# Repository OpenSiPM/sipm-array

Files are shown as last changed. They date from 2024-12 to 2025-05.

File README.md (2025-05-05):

# sipm-array
Schematics and layouts for SiPM arrays

# tia-s14160-x4
This contains schematics and PCB layouts for a 4 channel SiPM detection board used for parallel laser scanning.  Each channel implements the standard OpenSiPM transimpedance amplifier, pole zero cancelation, and low pass filtering to produce a Gaussian single photon response.  



# impulse response
X4-33nh-3 0-30-lpf-470nh-100pf (channel3)

# power supply
The X4 design uses the standard OpenSiPM power supply and bias generator boards.  Due to the higher current from running 4 SiPMs in parallel, the LT8362 bias generator is recommended for maximum dynamic range, although both designs will work.  Additionally the board can be configured to use two separate power supplies by ommitting resistors and plugging in two supply boards to both sockets.  However, in normal useage this is not required and is probably not useful as the current demand is low enough that a single supply is adquate.

# Non-descanned detection arm
Zemax simulation for non-descanned detection using the 4 channel SiPM board and the prescription for the lens array used can be found [here](https://github.com/OpenSiPM/sipm-array/tree/main/Zemax). 

# publication
A manuscript is forthcoming.

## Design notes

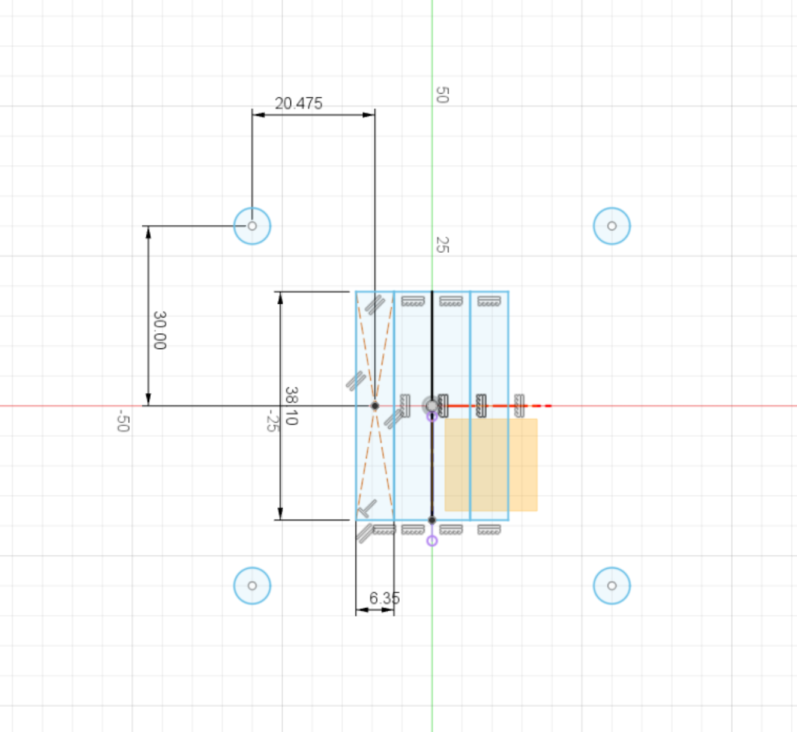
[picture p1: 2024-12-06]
mechanical diagram.png

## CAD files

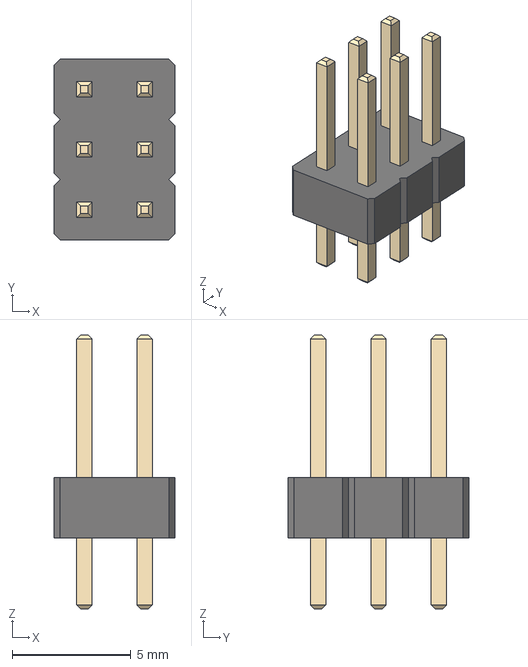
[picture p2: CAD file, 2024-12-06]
step/PinHeader_2x03_P2.54mm_Vertical.step
5.08 x 7.62 x 11.5 mm

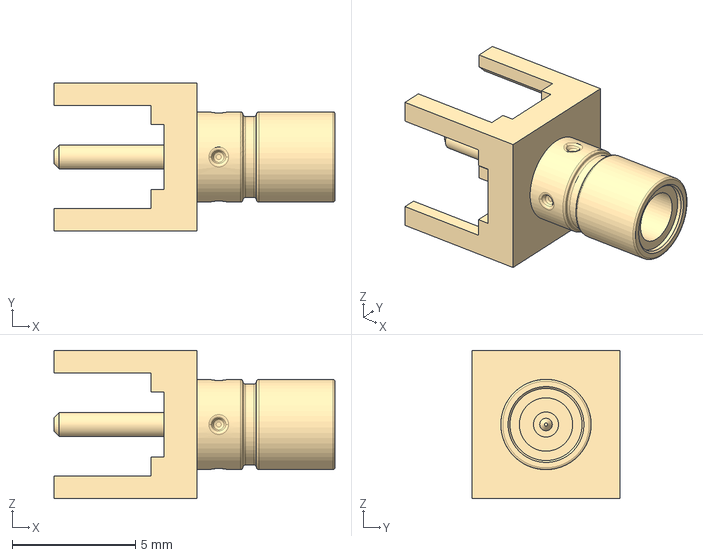
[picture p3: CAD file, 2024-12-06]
step/131-3701-261.stp
11.4 x 5.99 x 5.99 mm

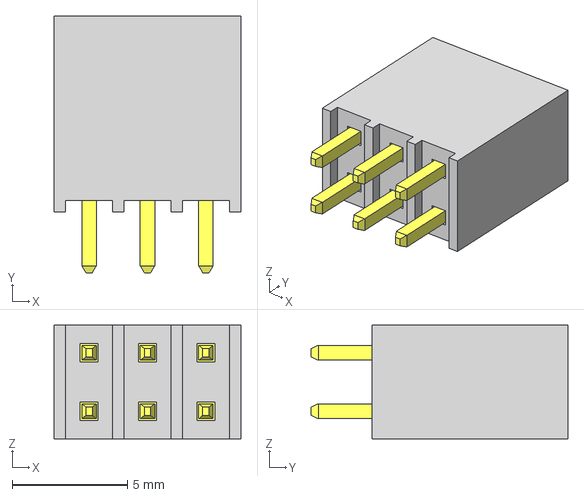
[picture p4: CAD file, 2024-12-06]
step/SSQ-103-01-G-D.step
8.13 x 11.2 x 4.95 mm
_T1SSQ-103-01-G-D
_P2SSQ-103-01-G-D

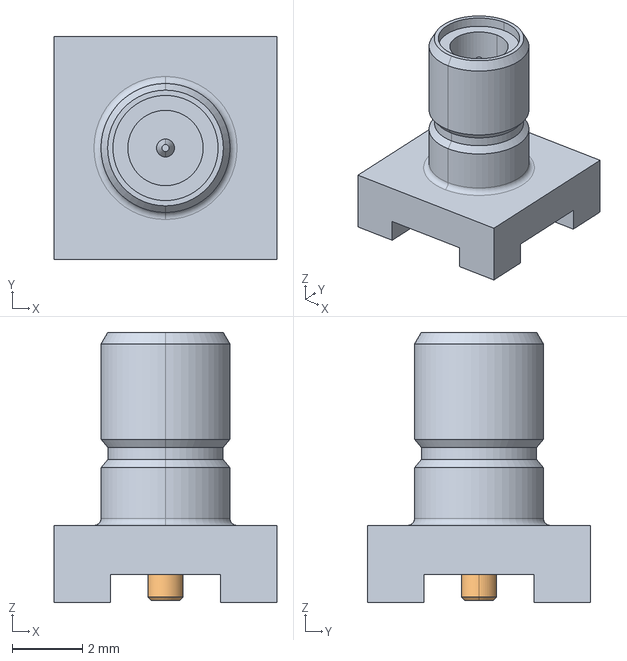
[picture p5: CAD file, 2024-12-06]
step/c-1-1337604-0-d-3d.stp
6.35 x 6.35 x 7.70 mm

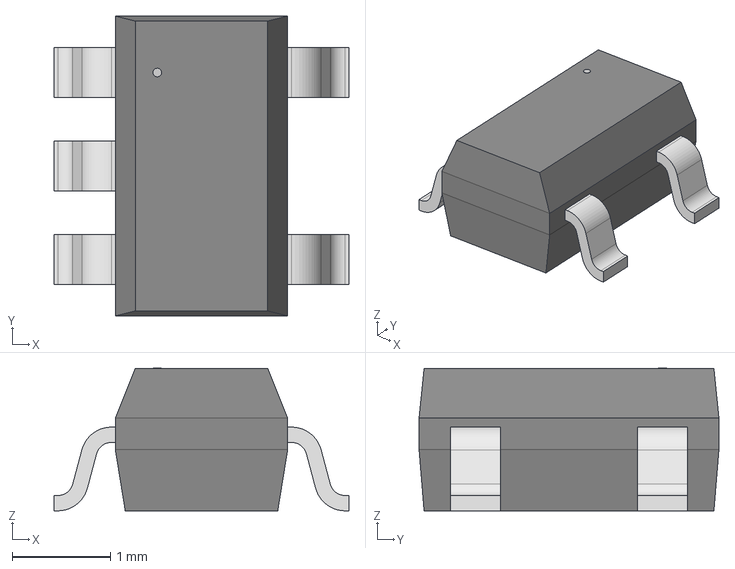
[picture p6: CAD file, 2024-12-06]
step/DBV5.step
3.00 x 3.05 x 1.45 mm

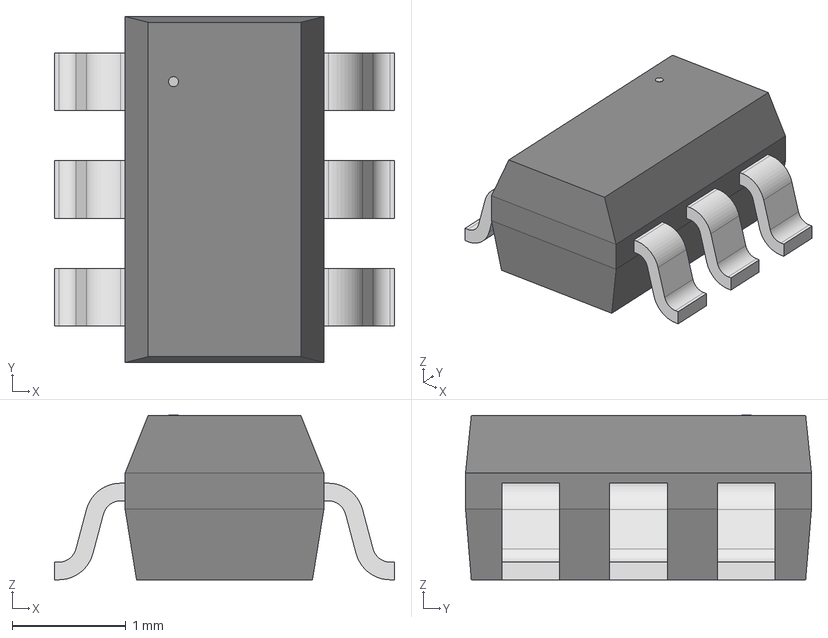
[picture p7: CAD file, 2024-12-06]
step/DBV6.step
3.00 x 3.05 x 1.45 mm

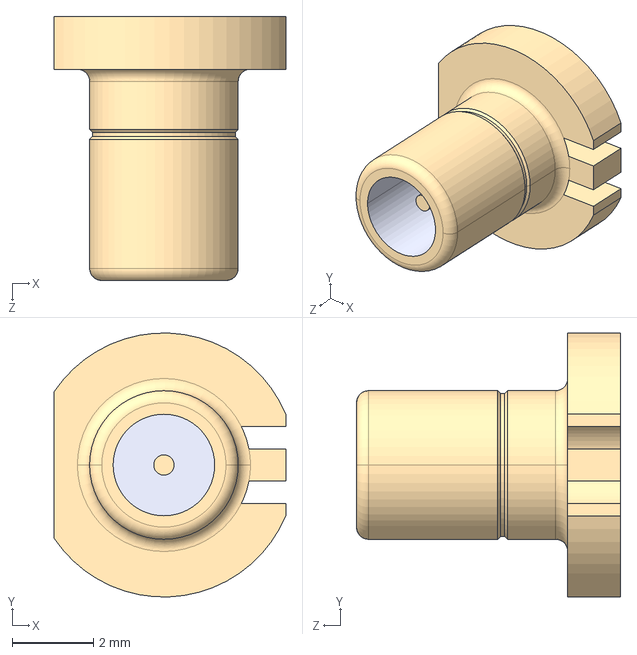
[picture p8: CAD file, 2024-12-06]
step/SMBR004D00.step
5.70 x 6.49 x 6.50 mm

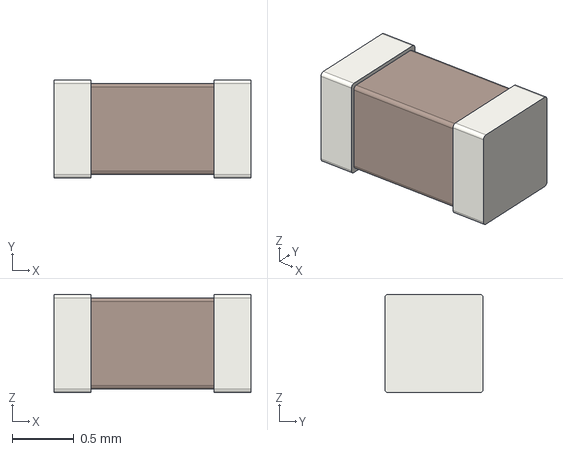
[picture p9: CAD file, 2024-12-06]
step/C_0603_1608Metric.step
1.60 x 0.8 x 0.8 mm

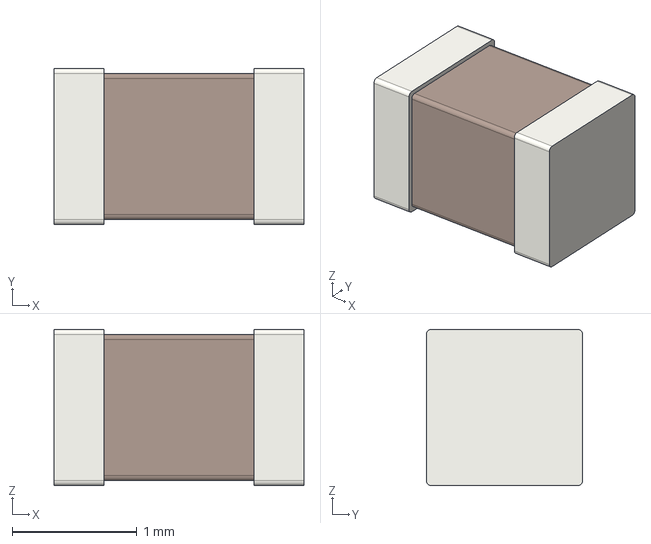
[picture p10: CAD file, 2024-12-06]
step/C_0805_2012Metric.step
2.00 x 1.25 x 1.25 mm

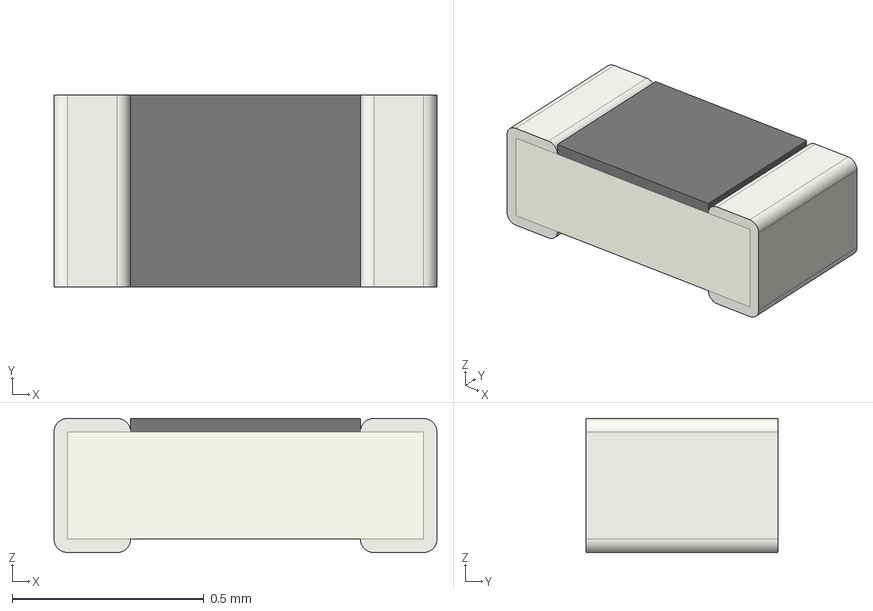
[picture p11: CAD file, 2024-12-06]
step/R_0402_1005Metric.step
1.00 x 0.5 x 0.35 mm

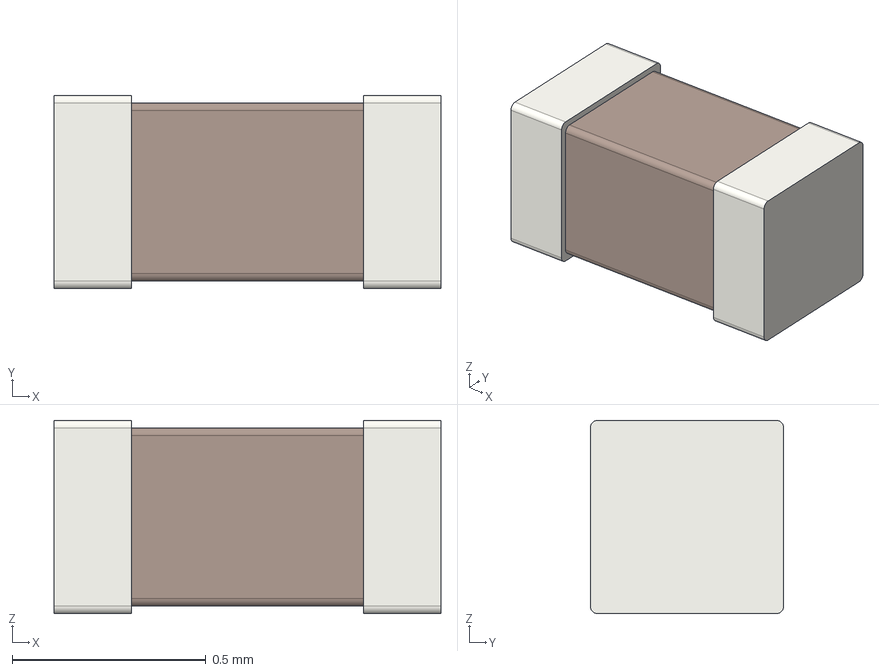
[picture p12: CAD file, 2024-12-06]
step/C_0402_1005Metric.step
1.00 x 0.5 x 0.5 mm

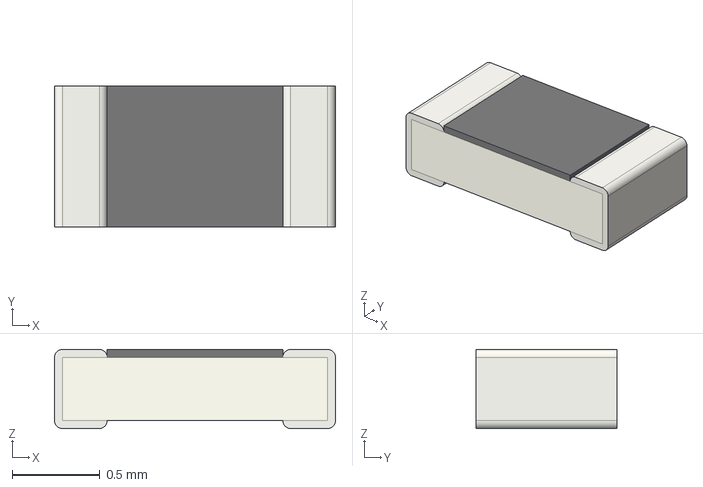
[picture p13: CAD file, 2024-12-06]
step/R_0603_1608Metric.step
1.60 x 0.8 x 0.45 mm

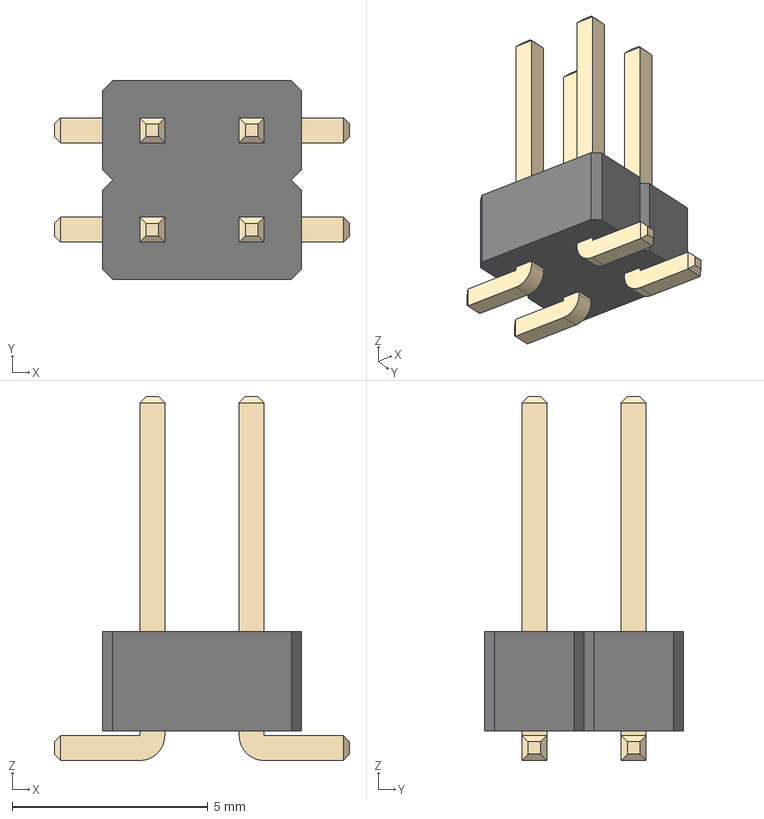
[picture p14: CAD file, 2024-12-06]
step/PinHeader_2x02_P2.54mm_Vertical_SMD.step
7.54 x 5.08 x 9.30 mm

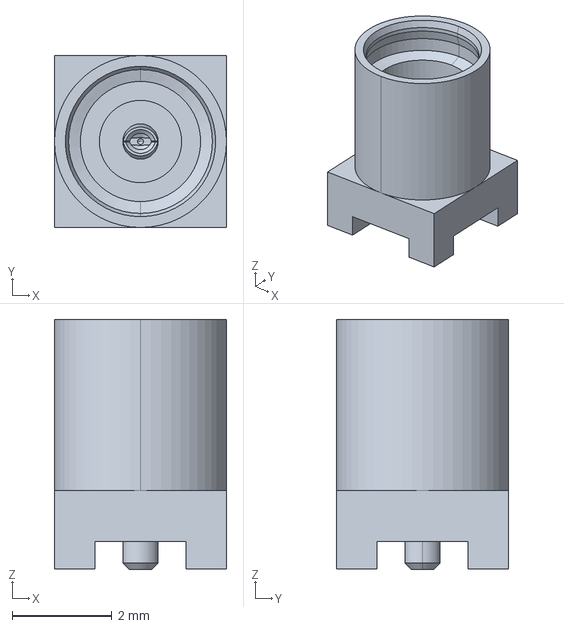
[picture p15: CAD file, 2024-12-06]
step/73415-2061.stp
3.45 x 3.45 x 5.01 mm

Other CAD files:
step/L_0603_1608Metric.step
step/S14160-3010PS_v3.step
step/S14160-3015PS v2.step
step/131-3701-261_old.stp
step/SMBR004D00.SLDPRT

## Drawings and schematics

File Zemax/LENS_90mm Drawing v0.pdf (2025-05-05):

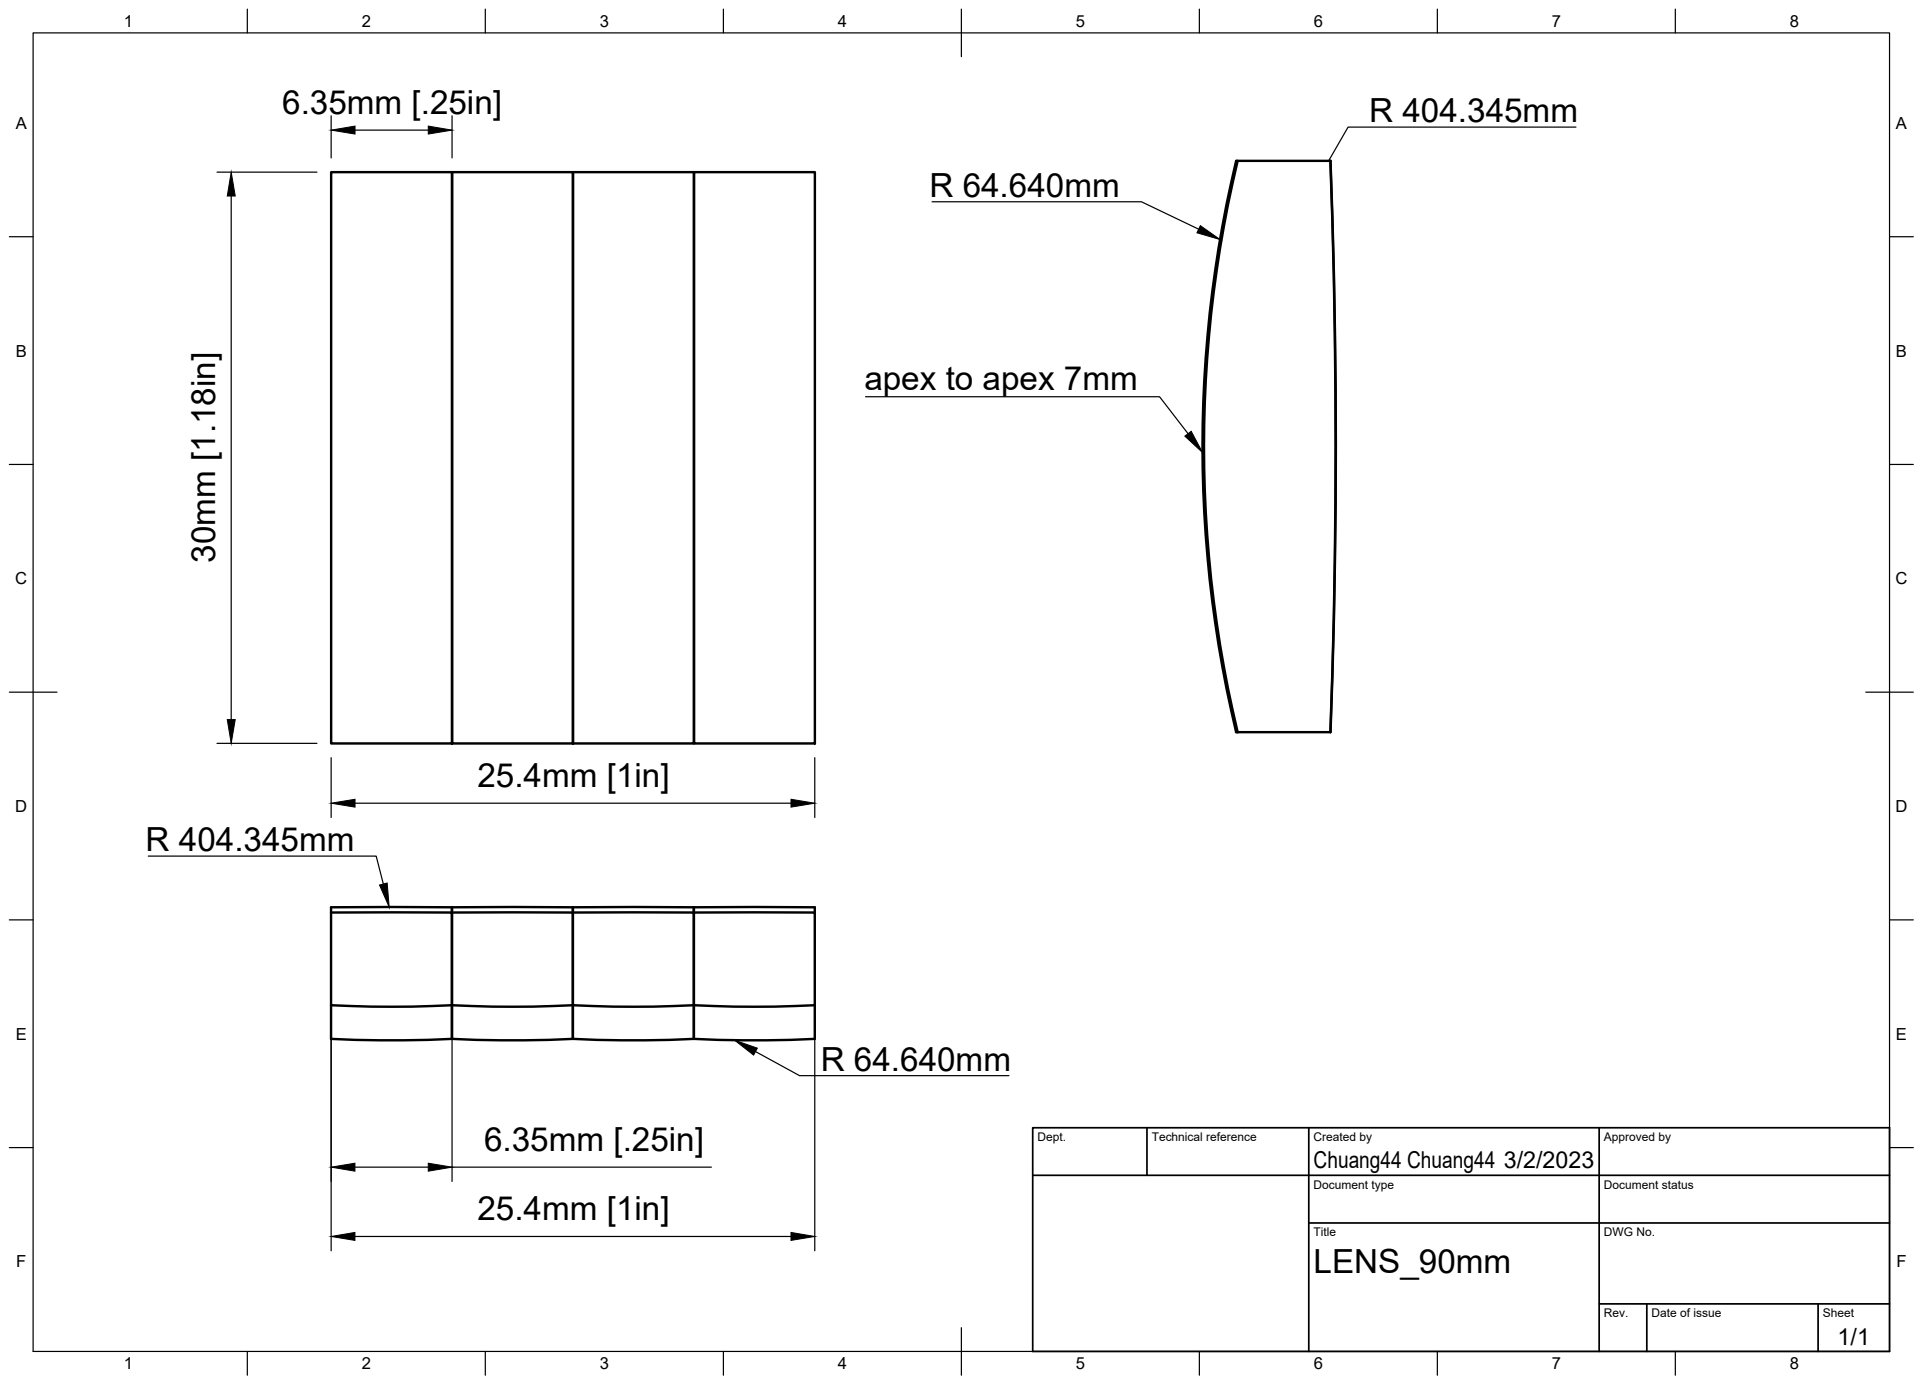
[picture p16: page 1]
Title; DWG No.; Rev.; Date of issue; Sheet; apex to apex 7mm

Dept. | Technical reference | Created by Chuang44 Chuang44 3/2/2023 | Approved by

Document type | Document status

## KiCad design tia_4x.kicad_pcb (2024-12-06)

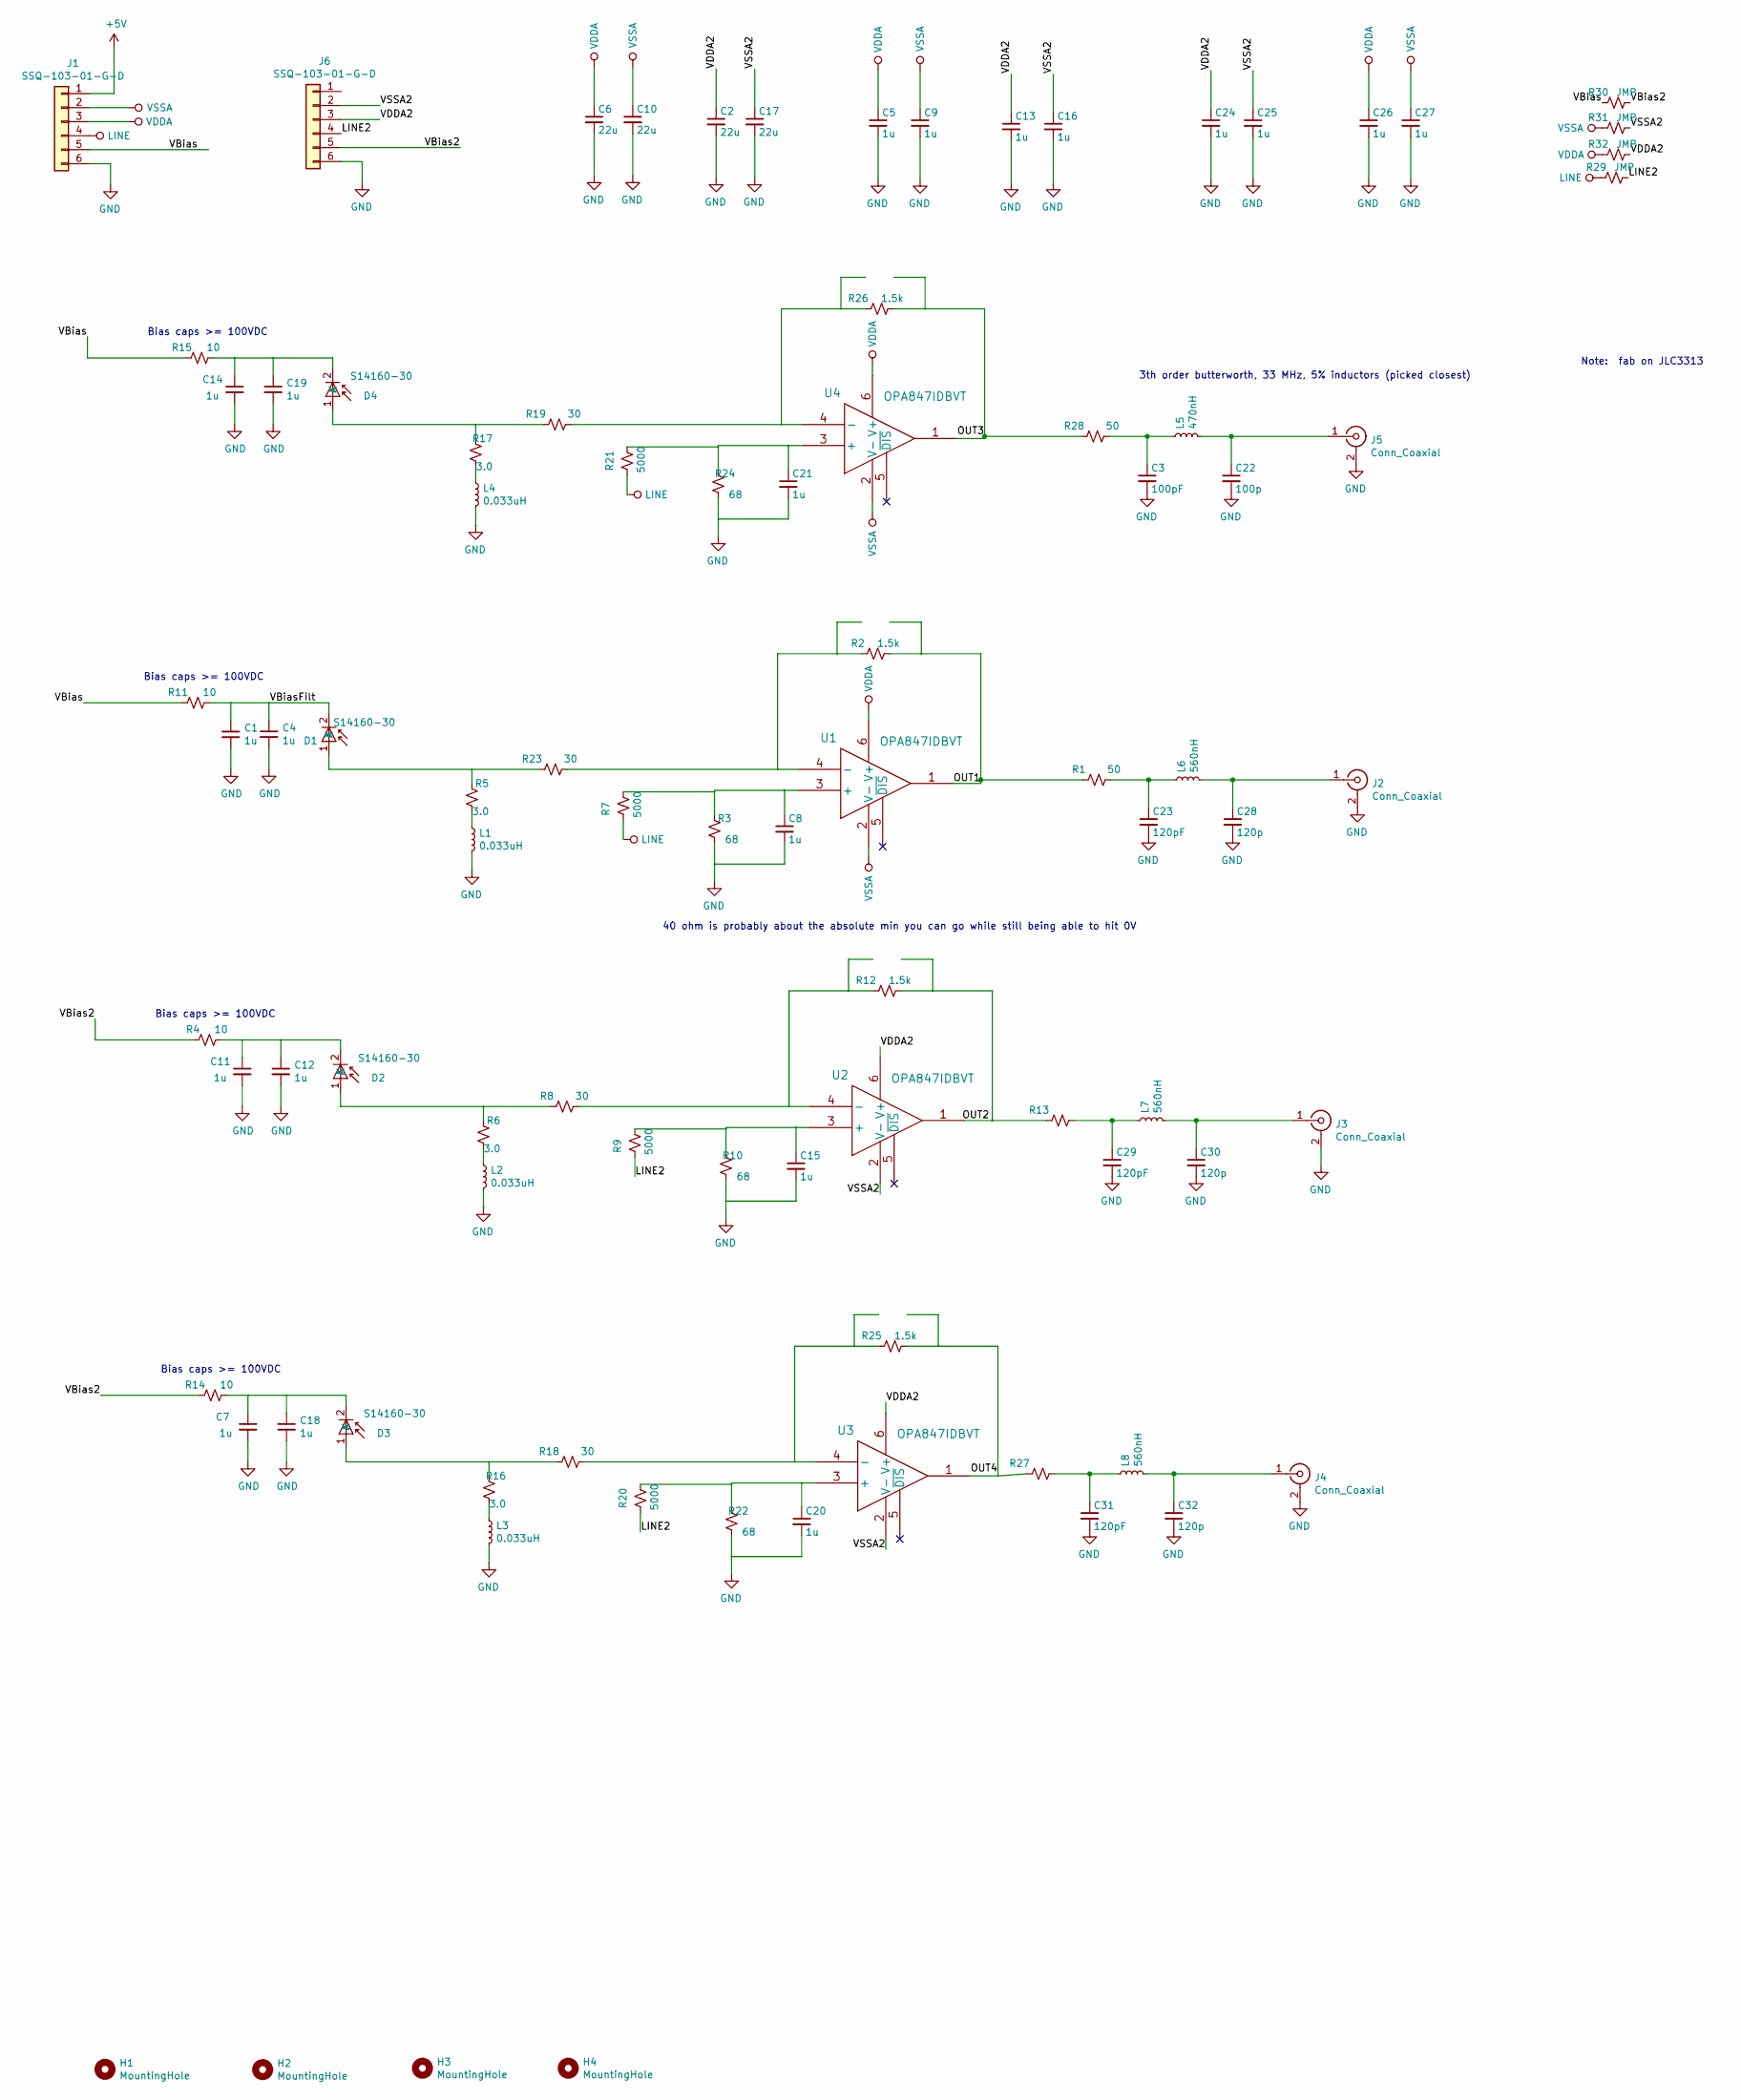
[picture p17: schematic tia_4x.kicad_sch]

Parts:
C1, C4, C7, C11, C12, C14, C18, C19: 1u; C_1206_3216Metric
C2, C6, C10, C17: 22u; C_0603_1608Metric
C3: 100pF; C_0402_1005Metric
C5, C8, C9, C13, C15, C16, C20, C21, C24, C25, C26, C27: 1u; C_0402_1005Metric
C22: 100p; C_0402_1005Metric
C23, C29, C31: 120pF; C_0402_1005Metric
C28, C30, C32: 120p; C_0402_1005Metric
D1, D2, D3, D4: S14160-30
H1, H2, H3, H4: MountingHole; MountingHole_6mm
J1, J6: SSQ-103-01-G-D; PinHeader_2x03_P2.54mm_Vertical
J2, J3, J4, J5: Conn_Coaxial; SMB_Jack_Vertical; Digikey WM5528-ND
L1, L2, L3, L4: 0.033uH; L_0603_1608Metric
L5: 470nH; L_0402_1005Metric; part MLF1005GR56JTD25
L6, L7, L8: 560nH; L_0402_1005Metric; part MLF1005GR56JTD25
R1, R13, R27, R28: 50; R_0402_1005Metric
R2, R12, R25, R26: 1.5k; R_0402_1005Metric
R3, R10, R22, R24: 68; R_0402_1005Metric
R4, R11, R14, R15: 10; R_0402_1005Metric
R5, R6, R16, R17: 3.0; R_0402_1005Metric
R7, R9, R20, R21: 5000; R_0402_1005Metric
R8, R18, R19, R23: 30; R_0402_1005Metric
R29, R30, R31, R32: JMP; R_0402_1005Metric
U1, U2, U3, U4: OPA847IDBVT

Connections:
+5V: J1.1
/LINE2: J6.4, R9.2, R20.2, R29.2
/OUT1: R1.1, R2.2, U1.1
/OUT2: R12.2, R13.1, U2.1
/OUT3: R26.2, R28.1, U4.1
/OUT4: R25.2, R27.1, U3.1
/VBias: J1.5, R11.1, R15.1, R30.1
/VBias2: J6.5, R4.1, R14.1, R30.2
/VBiasFilt: C1.1, C4.1, D1.2 (K), R11.2
/VDDA2: C2.1, C13.1, C24.1, J6.3, R32.2, U2.6 (V+), U3.6 (V+)
/VSSA2: C16.1, C17.1, C25.1, J6.2, R31.2, U2.2 (V-), U3.2 (V-)
GND: C1.2, C2.2, C3.2, C4.2, C5.2, C6.2, C7.2, C8.2, C9.2, C10.2, C11.2, C12.2, C13.2, C14.2, C15.2, C16.2, C17.2, C18.2, C19.2, C20.2, C21.2, C22.2, C23.2, C24.2, C25.2, C26.2, C27.2, C28.2, C29.2, C30.2, C31.2, C32.2, J1.6, J2.2 (Ext), J3.2 (Ext), J4.2 (Ext), J5.2 (Ext), J6.6, L1.2, L2.2, L3.2, L4.2, R3.1, R10.1, R22.1, R24.1
LINE: J1.4, R7.2, R21.2, R29.1
unnamed: C3.1, L5.1, R28.2
unnamed: C23.1, L6.1, R1.2
unnamed: C29.1, L7.1, R13.2
unnamed: C31.1, L8.1, R27.2
unnamed: D1.1 (A), R5.2, R23.1
unnamed: D2.1 (A), R6.2, R8.1
unnamed: C11.1, C12.1, D2.2 (K), R4.2
unnamed: D3.1 (A), R16.2, R18.1
unnamed: C7.1, C18.1, D3.2 (K), R14.2
unnamed: D4.1 (A), R17.2, R19.1
unnamed: C14.1, C19.1, D4.2 (K), R15.2
unnamed: C28.1, J2.1 (In), L6.2
unnamed: C30.1, J3.1 (In), L7.2
unnamed: C32.1, J4.1 (In), L8.2
unnamed: C22.1, J5.1 (In), L5.2
unnamed: L1.1, R5.1
unnamed: L2.1, R6.1
unnamed: L3.1, R16.1
unnamed: L4.1, R17.1
unnamed: C8.1, R3.2, R7.1, U1.3 (+)
unnamed: R2.1, R23.2, U1.4 (-)
unnamed: C15.1, R9.1, R10.2, U2.3 (+)
unnamed: R8.2, R12.1, U2.4 (-)
unnamed: C20.1, R20.1, R22.2, U3.3 (+)
unnamed: R18.2, R25.1, U3.4 (-)
unnamed: C21.1, R21.1, R24.2, U4.3 (+)
unnamed: R19.2, R26.1, U4.4 (-)
VDDA: C5.1, C6.1, C26.1, J1.3, R32.1, U1.6 (V+), U4.6 (V+)
VSSA: C9.1, C10.1, C27.1, J1.2, R31.1, U1.2 (V-), U4.2 (V-)

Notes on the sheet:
40 ohm is probably about the absolute min you can go while still being able to hit 0V
Bias caps >= 100VDC
3th order butterworth, 33 MHz, 5% inductors (picked closest)
Note: fab on JLC3313

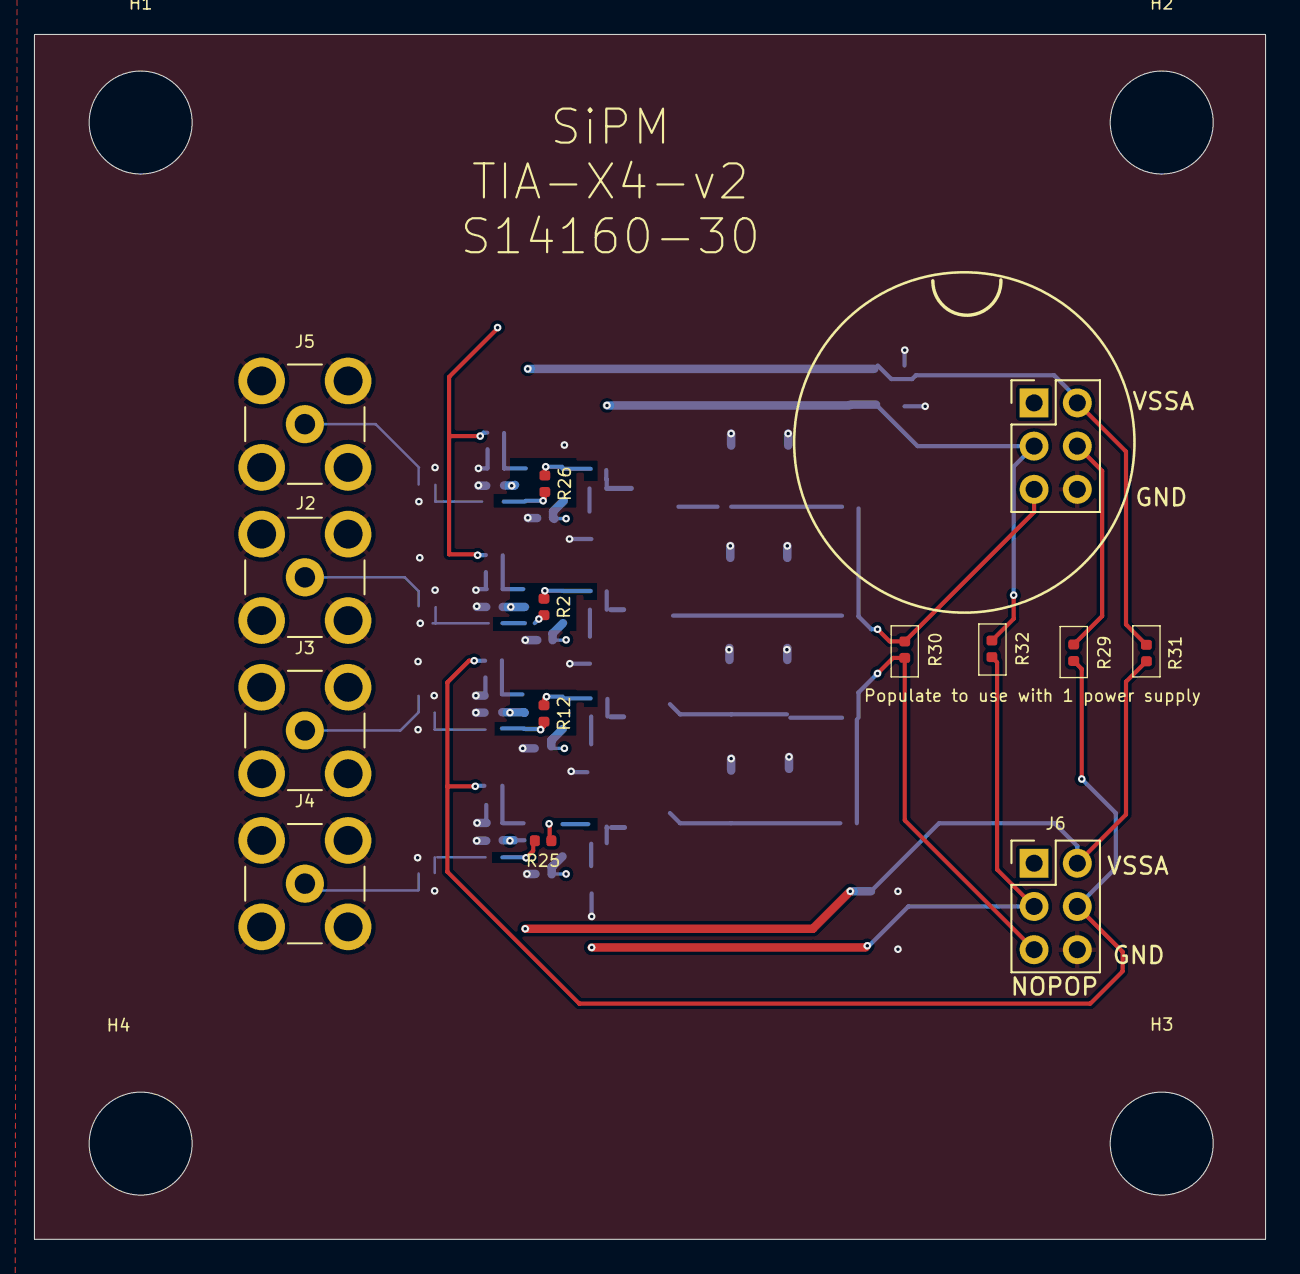
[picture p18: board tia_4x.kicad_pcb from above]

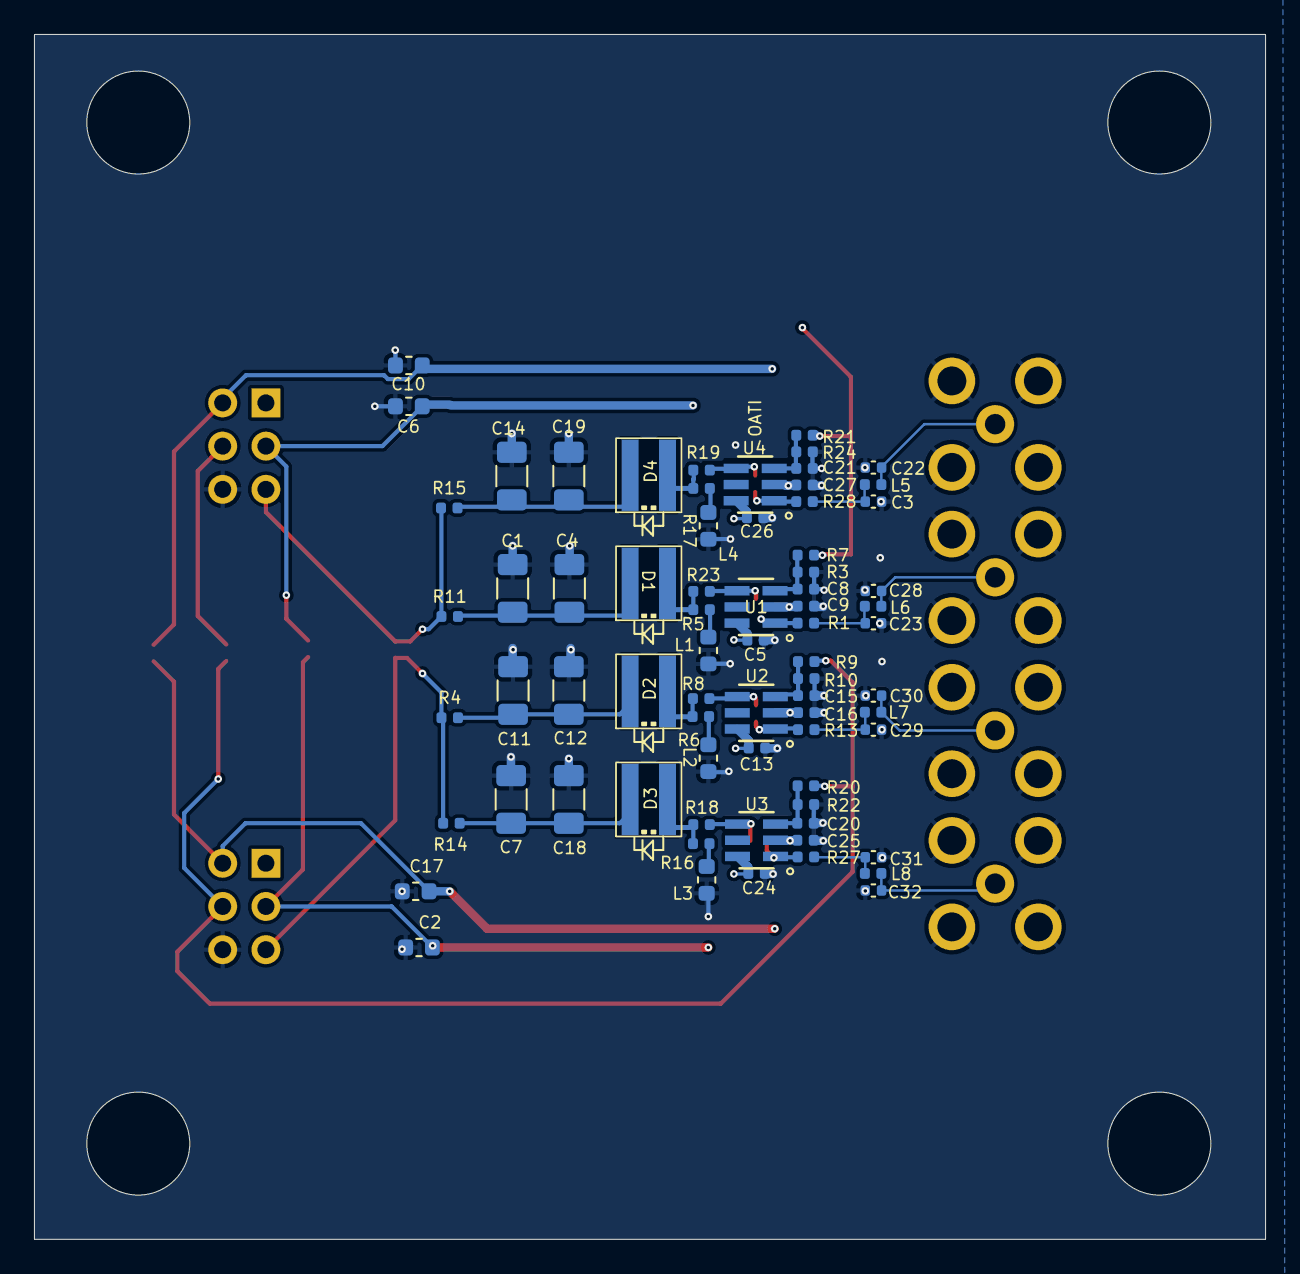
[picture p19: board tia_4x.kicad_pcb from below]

Board: 4 copper layers, 72.3 x 70.8 mm, 90 parts (72 on the bottom side), 41 nets.

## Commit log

2024-12-06 Initial upload for 4x SiPM board for parallel scanning
    [131-3701-261.stp, 131-3701-261_old.stp, 73415-2061.stp, C_0402_1005Metric.step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]
2025-05-05 Add Zemax simulation files for the non descanned detection arm and the lens array prescription

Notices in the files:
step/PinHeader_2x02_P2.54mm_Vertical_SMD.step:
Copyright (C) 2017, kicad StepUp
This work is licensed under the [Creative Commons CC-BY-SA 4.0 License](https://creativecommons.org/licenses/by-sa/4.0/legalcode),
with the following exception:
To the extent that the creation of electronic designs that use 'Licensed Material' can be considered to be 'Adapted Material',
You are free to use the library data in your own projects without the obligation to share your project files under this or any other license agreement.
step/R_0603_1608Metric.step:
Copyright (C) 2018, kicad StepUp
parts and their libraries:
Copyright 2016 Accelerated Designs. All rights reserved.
